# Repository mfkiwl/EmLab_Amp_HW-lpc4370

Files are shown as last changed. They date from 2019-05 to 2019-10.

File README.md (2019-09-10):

# EmLab Amp HW
Hardware for 80dB amp + digitizer

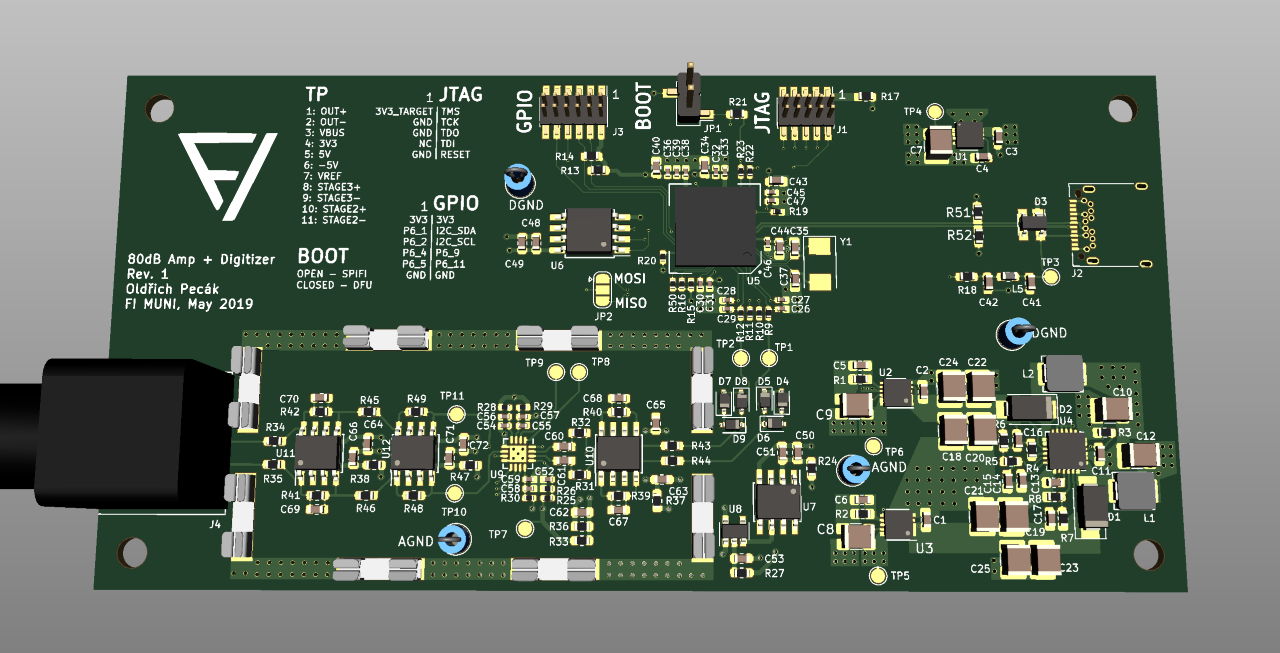
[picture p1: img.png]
Current Revision


## Notes
- the TPS65131 regulator does some weird stuff - maybe exchange for similar AD part?

## TODO
- debug prototype

### Schematic
- nothing

### PCB
- nothing

## Links
- [BOM](https://octopart.com/bom-tool/Xo4yGKYB)
- [LPC Link 2 Schematic](https://www.nxp.com/downloads/en/schematics/LPC-Link2-SCH.pdf)
- [BGA PCB Guidelines](https://www.nxp.com/docs/en/application-note/AN10778.pdf)
- [Proper grounding #1](https://www.analog.com/en/analog-dialogue/articles/staying-well-grounded.html)
- [Proper grounding #2](https://www.maximintegrated.com/en/app-notes/index.mvp/id/5450)
- [LPC4370 Datasheet](https://www.nxp.com/docs/en/data-sheet/LPC4370.pdf)
- [W25Q80BVSSIG Datasheet](https://openwrt.org/_media/media/datasheets/flash/w25q80bv.pdf)
- [IS25LP080D-JNLA3-TR](https://cz.mouser.com/ProductDetail/ISSI/IS25LP080D-JNLA3-TR?qs=sGAEpiMZZMuIiYGg9i1FDOSOPk6CUsSSrSt5PkokTOpe%2F19c4PAU8Q%3D%3D)
- [LT3094 Datasheet](https://www.analog.com/media/en/technical-documentation/data-sheets/LT3094.pdf)
- [LT3045 Datasheet] (https://www.analog.com/media/en/technical-documentation/data-sheets/3045fa.pdf)
- [TPS7A80 Datasheet](http://www.ti.com/lit/ds/symlink/tps7a80.pdf)
- [THS4131 Datasheet](http://www.ti.com/lit/ds/symlink/ths4131.pdf)
- [LMH6518 Datasheet](http://www.ti.com/lit/ds/symlink/lmh6518.pdf)

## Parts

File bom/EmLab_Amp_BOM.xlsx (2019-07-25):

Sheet: FARNELL
Počet desek: | 3 |  |  |  | Farnell
Manufacturer |  | Line Item | Počet(1 deska) | Celkem počet | URL
GCT |  | USB4085-GF-A | 1 | 3 | https://cz.farnell.com/gct-global-connector-technology/usb4085-gf-a/usb-connector-2-0-type-c-rcpt/dp/2924867
TE Connectivity |  | 1-1337543-0 | 1 | 3 | https://cz.farnell.com/greenpar-te-connectivity/1-1337543-0/rf-coaxial-bnc-right-angle-jack/dp/1020955
Vishay |  | CRCW04022K20FKED | 3 | 9 | https://cz.farnell.com/vishay/crcw04022k20fked/res-2k2-1-0-063w-0402-thick-film/dp/2140802
Vishay |  | CRCW04024K70FKEDHP | 3 | 9 | https://cz.farnell.com/vishay/crcw04024k70fkedhp/res-4k7-1-200mw-0402-thick-film/dp/1738858
Multicomp |  | MCWR04X1212FTL | 1 | 3 | https://cz.farnell.com/multicomp/mcwr04x1212ftl/res-12k1-1-0-0625w-thick-film/dp/2447105
Multicomp |  | MCWR06W1R00FTL | 2 | 6 | https://cz.farnell.com/multicomp/mcwr06w1r00ftl/res-1r-1-0-1w-0603-thick-film/dp/2447289
Vishay |  | CRCW060349R9FKEA | 2 | 6 | https://cz.farnell.com/vishay/crcw060349r9fkea/res-49r9-1-0-1w-0603-thick-film/dp/1469817
Multicomp |  | MCWR06X1000FTL | 2 | 6 | https://cz.farnell.com/multicomp/mcwr06x1000ftl/res-100r-1-0-1w-0603-thick-film/dp/2447227
Vishay |  | CRCW0603402RFKEA | 6 | 18 | https://cz.farnell.com/vishay/crcw0603402rfkea/res-402r-1-0-1w-0603-thick-film/dp/2141337
Vishay |  | CRCW06031K00FKEA | 1 | 3 | https://cz.farnell.com/vishay/crcw06031k00fkea/res-1k-1-0-1w-0603-thick-film/dp/1469740
Multicomp |  | MCWR06X2201FTL | 1 | 3 | https://cz.farnell.com/multicomp/mcwr06x2201ftl/res-2k2-1-0-1w-thick-film/dp/2447320
Vishay |  | CRCW06034K02FKEA | 7 | 21 | https://cz.farnell.com/vishay/crcw06034k02fkea/res-4k02-1-0-1w-0603-thick-film/dp/1469805
Multicomp |  | MCWR06X4701FTL | 2 | 6 | https://cz.farnell.com/multicomp/mcwr06x4701ftl/res-4k7-1-0-1w-0603-thick-film/dp/2447385
Vishay |  | CRCW060349K9FKEA | 2 | 6 | https://cz.farnell.com/vishay/crcw060349k9fkea/res-49k9-1-0-1w-0603-thick-film/dp/1652882
Multicomp |  | MCWR06X1003FTL | 1 | 3 | https://cz.farnell.com/multicomp/mcwr06x1003ftl/res-100k-1-0-1w-0603-thick-film/dp/2447226
Multicomp |  | MCWR06X1303FTL | 2 | 6 | https://cz.farnell.com/multicomp/mcwr06x1303ftl/res-130k-1-0-1w-thick-film/dp/2447247
Multicomp |  | MCWR06X5363FTL | 1 | 3 | https://cz.farnell.com/multicomp/mcwr06x5363ftl/res-536k-1-0-1w-0603-thick-film/dp/2694894
Panasonic |  | ERJ-3EKF6653V | 1 | 3 | https://cz.farnell.com/panasonic/erj3ekf6653v/res-665k-1-100mw-0603-thick-film/dp/2303304
Multicomp |  | MCWR06X1004FTL | 2 | 6 | https://cz.farnell.com/multicomp/mcwr06x1004ftl/res-1m-1-0-1w-0603-thick-film/dp/2447285
Multicomp |  | MC0402B104K250CT | 10 | 30 | https://cz.farnell.com/multicomp/mc0402b104k250ct/cap-0-1-f-25v-10-x7r-0402/dp/2320759
KEMET |  | C0402C470J5GACTU | 4 | 12 | https://cz.farnell.com/kemet/c0402c470j5gactu/cap-47pf-50v-5-c0g-np0-0402/dp/1414592
KEMET |  | C0402C103K3RACTU | 3 | 9 | https://cz.farnell.com/kemet/c0402c103k3ractu/cap-0-01-f-25v-10-x7r-0402/dp/1650806
Murata |  | GCM155R71E223KA55D | 2 | 6 | https://cz.farnell.com/murata/gcm155r71e223ka55d/cap-0-022-f-25v-10-x7r-0402/dp/2494188
KEMET |  | C0402C332K5RACTU | 1 | 3 | https://cz.farnell.com/kemet/c0402c332k5ractu/cap-3300pf-50v-10-x7r-0402/dp/1414590
KEMET |  | C0603C104M5RACTU | 12 | 36 | https://cz.farnell.com/kemet/c0603c104m5ractu/cap-0-1-f-50v-20-x7r-0603/dp/2581046
Murata |  | GRM188R61A106ME69D | 8 | 24 | https://cz.farnell.com/murata/grm188r61a106me69d/cap-10-f-10v-20-x5r-0603/dp/2456110
Yageo |  | CC0603KRX5R5BB475 | 3 | 9 | https://cz.farnell.com/yageo/cc0603krx5r5bb475/cap-4-7-f-6-3v-10-x5r-0603/dp/9402110
TDK |  | CGA3E3X7R1E474K080AB | 2 | 6 | https://cz.farnell.com/tdk/cga3e3x7r1e474k080ab/cap-0-47-f-25v-10-x7r-0603/dp/2210923
KEMET |  | C0603C103M5RACTU | 2 | 6 | https://cz.farnell.com/kemet/c0603c103m5ractu/cap-0-01-f-50v-20-x7r-0603/dp/2581043
KEMET |  | C0603C120J5GACTU | 2 | 6 | https://cz.farnell.com/kemet/c0603c120j5gactu/cap-12pf-50v-5-c0g-np0-0603/dp/1414612
KEMET |  | C0603C180J5GACAUTO | 2 | 6 | https://cz.farnell.com/kemet/c0603c180j5gacauto/cap-18pf-50v-5-c0g-np0-0603/dp/2821267
KEMET |  | C0603C680J5GACAUTO | 2 | 6 | https://cz.farnell.com/kemet/c0603c680j5gacauto/cap-68pf-50v-5-c0g-np0-0603/dp/2821269
Vishay |  | VJ0603A470KXAAC | 2 | 6 | https://cz.farnell.com/vishay/vj0603a470kxaac/cap-47pf-50v-10-c0g-np0-0603/dp/2896694
Murata |  | GCJ188R71E105KA01D | 1 | 3 | https://cz.farnell.com/murata/gcj188r71e105ka01d/cap-1-f-25v-10-x7r-0603/dp/2781410
KEMET |  | C0603C224K3RECAUTO | 1 | 3 | https://cz.farnell.com/kemet/c0603c224k3recauto/cap-0-22-f-25v-10-x7r-0603/dp/2708702

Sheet: MOUSER
Počet desek: | 3 |  |  |  | Mouser
Manufacturer |  | Line Item | Počet(1 deska) | Celkem počet | URL
NXP Semiconductors |  | LPC4370FET100E | 1 | 3 | https://cz.mouser.com/ProductDetail/NXP-Semiconductors/LPC4370FET100E
ISSI |  | IS25LP080D-JBLE | 1 | 3 | https://cz.mouser.com/ProductDetail/ISSI/IS25LP080D-JBLE
Texas Instruments |  | LMH6518SQE/NOPB | 1 | 3 | https://cz.mouser.com/ProductDetail/Texas-Instruments/LMH6518SQE-NOPB
Texas Instruments |  | THS4131ID | 3 | 9 | https://cz.mouser.com/ProductDetail/Texas-Instruments/THS4131ID?qs=sGAEpiMZZMsFOcXqMdeHCUfrMGQl6bAspOAcQWpNFhs%3D
Texas Instruments |  | TPS65131RGER | 1 | 3 | https://cz.mouser.com/ProductDetail/Texas-Instruments/TPS65131RGER
Analog Devices / Linear Technology |  | LT3094IDD#PBF | 1 | 3 | https://cz.mouser.com/ProductDetail/Analog-Devices-Linear-Technology/LT3094IDDPBF?qs=sGAEpiMZZMsGz1a6aV8DcJ5wwoift2gCGfC6lWVApcc%3D
Analog Devices |  | LT3045EDD#PBF | 1 | 3 | https://cz.mouser.com/ProductDetail/Analog-Devices-Linear-Technology/LT3045EDDPBF?qs=sGAEpiMZZMsGz1a6aV8DcG0CZsy7SJKshm5FSsNz7hU%3D
Texas Instruments |  | TPS7A8033DRBT | 1 | 3 | https://cz.mouser.com/ProductDetail/Texas-Instruments/TPS7A8033DRBT
Abracon |  | ABM3-12.000MHZ-D2Y-T | 1 | 3 | https://cz.mouser.com/ProductDetail/ABRACON/ABM3-12000MHZ-D2Y-T
Microchip |  | MCP601RT-I/OT | 1 | 3 | https://cz.mouser.com/ProductDetail/Microchip-Technology/MCP601RT-I-OT
Analog Devices |  | ADR421ARZ | 1 | 3 | https://cz.mouser.com/ProductDetail/Analog-Devices/ADR421ARZ
Nexperia |  | PRTR5V0U2X,215 | 1 | 3 | https://cz.mouser.com/ProductDetail/Nexperia/PRTR5V0U2X215
Bourns |  | SRP4012TA-5R6M | 1 | 3 | https://cz.mouser.com/ProductDetail/Bourns/SRP4012TA-5R6M
Bourns |  | SRP4012TA-4R7M | 1 | 3 | https://cz.mouser.com/ProductDetail/Bourns/SRP4012TA-4R7M
Harwin |  | S01-50250500 | 1 | 3 | https://cz.mouser.com/ProductDetail/Harwin/S01-50250500
Harwin |  | S2711-46R | 8 | 24 | https://cz.mouser.com/ProductDetail/Harwin/S2711-46R
MCC |  | SK34A-TP | 2 | 6 | https://cz.mouser.com/ProductDetail/Micro-Commercial-Components-MCC/SK34A-TP
Molex |  | 87898-0204 | 1 | 3 | https://cz.mouser.com/ProductDetail/Molex/87898-0204
FCI |  | 20021121-00010C4LF | 1 | 3 | https://cz.mouser.com/ProductDetail/Amphenol-FCI/20021121-00010C4LF
FCI |  | 20021121-00012C4LF | 1 | 3 | https://cz.mouser.com/ProductDetail/Amphenol-FCI/20021121-00012C4LF
Keystone |  | 5006 | 4 | 12 | https://cz.mouser.com/ProductDetail/Keystone-Electronics/5006
Diodes Inc. |  | 1N4148WS-7-F | 6 | 18 | https://cz.mouser.com/ProductDetail/Diodes-Incorporated/1N4148WSF-7
Yageo |  | RC0402FR-07100RL | 4 | 12 | https://cz.mouser.com/ProductDetail/Yageo/RC0402FR-07100RL
Yageo |  | RC0402FR-071RL | 3 | 9 | https://cz.mouser.com/ProductDetail/Yageo/RC0402FR-071RL
Yageo |  | RC0402FR-0710KL | 2 | 6 | https://cz.mouser.com/ProductDetail/Yageo/RC0402FR-0710KL
KEMET |  | C1210C475K3RACTU | 11 | 33 | https://cz.mouser.com/ProductDetail/KEMET/C1210C475K3RACTU?qs=sGAEpiMZZMs0AnBnWHyRQKLP9quIYhdR8bSQJSyuECw%3D
Murata |  | GCM32ER71E106KA57L | 2 | 6 | https://cz.mouser.com/ProductDetail/Murata-Electronics/GCM32ER71E106KA57K
Murata |  | GCM155R71E393JA55D | 1 | 3 | https://cz.mouser.com/ProductDetail/Murata-Electronics/GCM155R71E393JA55D
TDK |  | C1608X5R1E335K080AC | 1 | 3 | https://cz.mouser.com/ProductDetail/TDK/C1608X5R1E335K080AC

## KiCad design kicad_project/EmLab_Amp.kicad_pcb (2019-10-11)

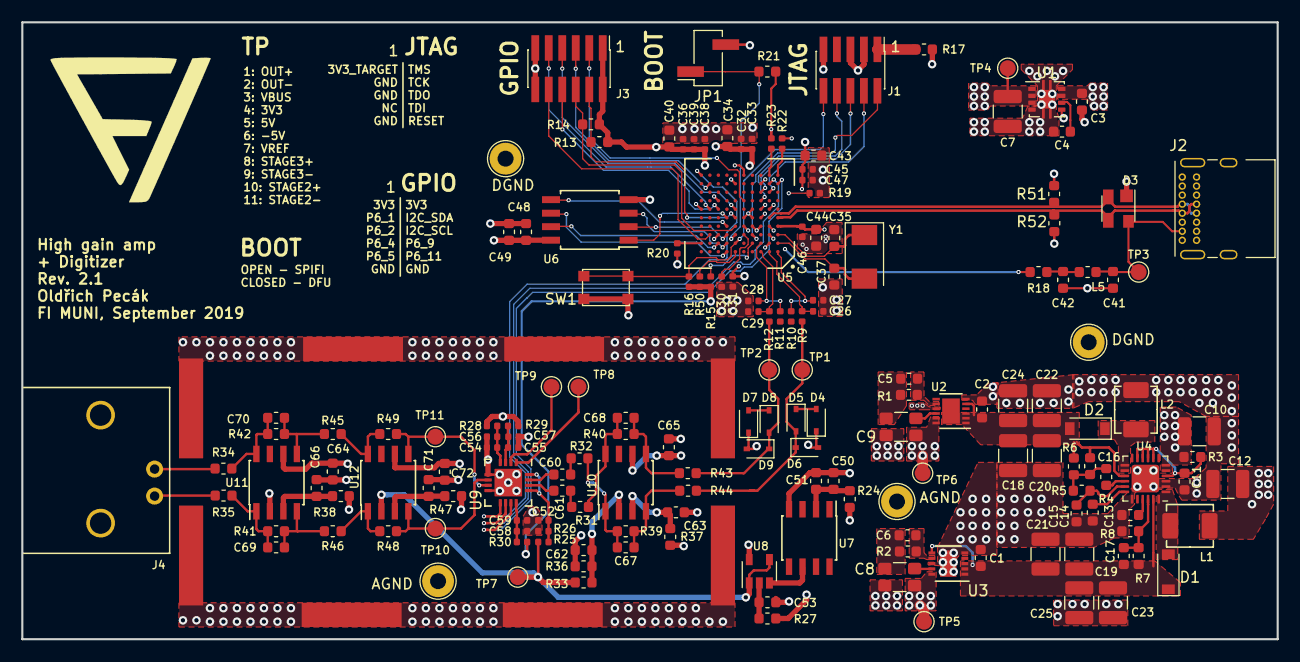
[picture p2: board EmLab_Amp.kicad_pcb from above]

Board: 4 copper layers, 118.1 x 58.0 mm, 170 parts (0 on the bottom side), 95 nets.

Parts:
AGND: TestPoint_Loop_D2.54mm_Drill1.5mm_Beaded
AGND#2: TestPoint_Loop_D2.54mm_Drill1.5mm_Beaded
C1, C2: 470n; C_0603_1608Metric
C3: 1u; C_0603_1608Metric
C4, C13: 10n; C_0603_1608Metric
C5, C6, C14: 4u7; C_0603_1608Metric
C7, C10, C12, C18, C19, C20, C21, C22, C23, C24, C25: 4u7; C_1210_3225Metric
C8, C9: 10u; C_1210_3225Metric_SPLIT
C11, C41, C48, C51, C53, C62, C63, C64, C65, C66, C71, C72: 100n; C_0603_1608Metric
C15: 220n; C_0603_1608Metric
C16, C17: 12p; C_0603_1608Metric
C26, C27, C28, C29: 47p; C_0402_1005Metric
C30, C31, C32, C36, C39, C45, C52, C56, C57, C58: 100n; C_0402_1005Metric
C33, C38: 22n; C_0402_1005Metric
C34, C40, C43, C44, C49, C50, C60, C61: 10u; C_0603_1608Metric
C35, C37: 18p; C_0603_1608Metric
C42: 3u3; C_0603_1608Metric
C46: 3n3; C_0402_1005Metric
C47: 39n; C_0402_1005Metric
C54, C55, C59: 10n; C_0402_1005Metric
C67, C68: 69p8; C_0603_1608Metric
C69, C70: 47p; C_0603_1608Metric
D1, D2: D_Schottky; D_SOD-123
D3: PRTR5V0U2X; SOT-143
D4, D5, D6, D7, D8, D9: 1N4148WS; D_SOD-323
DGND: TestPoint_Loop_D2.54mm_Drill1.5mm_Beaded
DGND#2: TestPoint_Loop_D2.54mm_Drill1.5mm_Beaded
J1: JTAG; PinHeader_2x05_P1.27mm_Vertical_SMD
J2: USB_C_Receptacle_USB2.0; USB_C_Receptacle_GCT_USB4085
J3: GPIO_EXP; PinHeader_2x06_P1.27mm_Vertical_SMD
J4: BNC; BNC_1337543
JP1: PinHeader_1x02_P2.54mm_Vertical_SMD_Pin1Right
L1: 4u7; BOURNS-SRP4012TA
L2: 5u6; BOURNS-SRP4012TA
L5: 1R resistor; L_0603_1608Metric
R1, R2: 49K9; R_0603_1608Metric
R3, R18: 100R; R_0603_1608Metric
R4: 100K; R_0603_1608Metric
R5, R8: 130K; R_0603_1608Metric
R6: 665K; R_0603_1608Metric
R7: 536K; R_0603_1608Metric
R9, R10, R11, R12: 100R; R_0402_1005Metric
R13, R14: 4K7; R_0603_1608Metric
R15, R16, R50: 4K7; R_0402_1005Metric
R17: 0R; R_0603_1608Metric
R19: 12K1; R_0402_1005Metric
R20, R22, R23: 2K2; R_0402_1005Metric
R21: 2K2; R_0603_1608Metric
R24, R27, R37, R38, R47: 1R; R_0603_1608Metric
R25, R26: 10K; R_0402_1005Metric
R28, R29, R30: 1R; R_0402_1005Metric
R31, R32, R34, R35, R45, R46: 400R; R_0603_1608Metric
R33, R39, R40, R48, R49: 4K; R_0603_1608Metric
R36: 1K; R_0603_1608Metric
R41, R42: 40K; R_0603_1608Metric
R43, R44: 50R; R_0603_1608Metric
R51, R52: 1M; R_0603_1608Metric
SW1: RST BTN; SW_SPST_PTS810
TP1: OUT+; TestPoint_Pad_D1.5mm
TP2: OUT-; TestPoint_Pad_D1.5mm
TP3: VBUS; TestPoint_Pad_D1.5mm
TP4: 3V3; TestPoint_Pad_D1.5mm
TP5: 5V; TestPoint_Pad_D1.5mm
TP6: -5V; TestPoint_Pad_D1.5mm
TP7: V_REF; TestPoint_Pad_D1.5mm
TP8: Stage3+; TestPoint_Pad_D1.5mm
TP9: Stage3-; TestPoint_Pad_D1.5mm
TP10: Stage2+; TestPoint_Pad_D1.5mm
TP11: Stage2-; TestPoint_Pad_D1.5mm
U1: TPS7A80; TI-VSON-8
U2: LT3094xDD; DFN-12-1EP_3x3mm_P0.45mm_EP1.66x2.38mm
U3: LT3045xDD; DFN-10-1EP_3x3mm_P0.5mm_EP1.55x2.48mm
U4: TPS6513x; QFN-24-1EP_4x4mm_P0.5mm_EP2.6x2.6mm
U5: LPC4370-TFBGA100; BGA-100_10x10_10.0x10.0mm
U6: IS25LP080D; SOIJ-8_5.3x5.3mm_P1.27mm
U7: ADR421; SOIC-8_3.9x4.9mm_P1.27mm
U8: MCP601R; SOT-23-5
U9: LMH6518; QFN-16-1EP_4x4mm_P0.5mm_EP2.6x2.6mm
U10, U11, U12: THS4131ID; SOIC-8_3.9x4.9mm_P1.27mm
Y1: 12MHz Crystal; Crystal_SMD_Abracon_ABM3-2Pin_5.0x3.2mm

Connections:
+3V3: C7.1, C31.1, C32.1, C33.1, C34.1, C36.1, C38.1, C39.1, C40.1, C43.1, C44.1, C45.1, C46.1, C47.1, C48.1, C49.1, J3.1, J3.2, R13.1, R14.1, R15.1, R16.1, R17.2, R21.1, R23.1, R30.1, R50.1, TP4.1, U1.1, U1.2, U1.3, U5.B2, U5.D1, U5.D2, U5.E4, U5.E5, U5.F4, U5.F10, U5.K5, U6.8
+5V: C8.2, R24.1, R27.1, R28.1, R29.1, R37.1, R38.1, R47.1, TP5.1, U3.9, U3.10
-5V: C9.2, C65.2, C66.2, C72.2, TP6.1, U2.10, U2.11, U2.12, U10.6, U11.6, U12.6
/Amplifier/S3_CS: U5.K10, U9.9
/Amplifier/S3_DIO: U5.J2, U9.10
/Amplifier/S3_SCLK: U5.J1, U9.11
/Amplifier/STAGE2_NEG: R49.2, TP11.1, U9.7, U12.5
/Amplifier/STAGE2_POS: R48.1, TP10.1, U9.6, U12.4
/Amplifier/V_REF: R25.1, R33.1, TP7.1, U8.1, U8.4, U12.2
/LPC4370-GPIO/BOOT_0: R23.2, U5.K2
/LPC4370-GPIO/BOOT_1: R22.1, U5.K1
/LPC4370-GPIO/BOOT_2: JP1.1, R21.2, U5.C6
/LPC4370-GPIO/BOOT_3: R20.1, U5.B10
/LPC4370-GPIO/GPIO_0: J3.3, U5.G5
/LPC4370-GPIO/GPIO_1: J3.5, U5.J9
/LPC4370-GPIO/GPIO_2: J3.7, U5.F6
/LPC4370-GPIO/GPIO_3: J3.9, U5.F9
/LPC4370-GPIO/GPIO_4: J3.8, U5.F8
/LPC4370-GPIO/GPIO_5: J3.10, U5.C9
/LPC4370-GPIO/I2C_SCL: J3.6, R14.2, U5.D6
/LPC4370-GPIO/I2C_SDA: J3.4, R13.2, U5.E6
/LPC4370-GPIO/SPIFI_CS: U5.E7, U6.1
/LPC4370-GPIO/SPIFI_MISO: U5.C7, U6.2
/LPC4370-GPIO/SPIFI_MOSI: U5.D7, U6.5
/LPC4370-GPIO/SPIFI_SCK: U5.A7, U6.6
/LPC4370-GPIO/SPIFI_SIO2: U5.B7, U6.3
/LPC4370-GPIO/SPIFI_SIO3: U5.B8, U6.7
/LPC4370-JTAG-PWR-MISC/ADC0: D5.2, D6.1, R9.2, R44.2, TP1.1
/LPC4370-JTAG-PWR-MISC/ADC3: D8.2, D9.1, R12.2, R43.1, TP2.1
/LPC4370-JTAG-PWR-MISC/DBGEN: R50.2, U5.A6
/LPC4370-JTAG-PWR-MISC/RESET: J1.10, R16.2, SW1.1, U5.B6
/LPC4370-JTAG-PWR-MISC/TCK: J1.4, U5.H2
/LPC4370-JTAG-PWR-MISC/TDI: J1.8, U5.G3
/LPC4370-JTAG-PWR-MISC/TDO: J1.6, U5.H3
/LPC4370-JTAG-PWR-MISC/TMS: J1.2, U5.C4
/LPC4370-JTAG-PWR-MISC/TRST: R15.2, U5.B4
/LPC4370-USB/USB_VBUS: C3.1, C10.1, C12.1, C41.1, D3.4, J2.A4, J2.A9, J2.B4, J2.B9, L1.1, L5.2, R3.2, TP3.1, U1.5, U1.7, U1.8, U4.5, U4.6
/Power/VNEG: C2.2, C16.2, C18.1, C20.1, C22.1, C24.1, D2.2, R6.2, U2.1, U2.2, U2.3, U2.5, U2.13, U4.15
/Power/VPOS: C1.2, C17.1, C19.1, C21.1, C23.1, C25.1, D1.1, R7.1, U3.1, U3.2, U3.3, U3.6, U4.23
GND: AGND.1, AGND#2.1, C1.1, C2.1, C3.2, C4.2, C5.1, C6.1, C7.2, C8.1, C9.1, C10.2, C11.2, C12.2, C13.2, C14.2, C15.2, C18.2, C19.2, C20.2, C21.2, C22.2, C23.2, C24.2, C25.2, C26.2, C27.2, C28.2, C29.2, C30.2, C31.2, C32.2, C33.2, C34.2, C35.2, C36.2, C37.2, C38.2, C39.2, C40.2, C41.2, C42.2, C43.2, C44.2, C45.2, C46.2, C47.2, C48.2, C49.2, C50.1, C51.1, C52.1, C53.1, C54.1, C55.1, C56.1, C57.1, C58.1, C59.1, C62.1, C63.1, C64.1, C65.1, C66.1, C71.1, C72.1, D3.1, D4.1, D6.2, D7.1, D9.2, DGND.1, DGND#2.1, J1.3, J1.5, J1.9, J2.A1, J2.A12, J2.B1, J2.B12, J2.S1, J3.11, J3.12, J4.2, JP1.2, L2.2, R1.1, R2.1, R8.2, R19.2, R20.2, R22.2, R26.1, R35.1, R36.1, R51.2, R52.2, SW1.2, U1.4, U1.9, U2.6, U2.9, U3.5, U3.8, U3.11, U4.2, U4.3, U4.19, U4.25, U5.C2, U5.C8, U5.D3, U5.D4, U5.D5, U5.F2, U5.G8, U5.J3, U5.J6, U6.4, U7.4, U8.5, U9.5, U9.8, U9.17, U11.2
unnamed: C4.1, U1.6
unnamed: C5.2, R1.2, U2.8
unnamed: C6.2, R2.2, U3.7
unnamed: C11.1, R3.1, U4.4, U4.8, U4.9, U4.10, U4.11
unnamed: C13.1, U4.21
unnamed: C14.1, U4.18
unnamed: C15.1, R5.1, U4.17
unnamed: C16.1, R4.1, R5.2, R6.1
unnamed: C17.2, R7.2, R8.1, U4.22
unnamed: C26.1, R9.1, U5.A2
unnamed: C27.1, R10.1, U5.A1
unnamed: C28.1, R11.1, U5.B3
unnamed: C29.1, R12.1, U5.A3
unnamed: C30.1, U5.C5
unnamed: C35.1, U5.C1, Y1.1
unnamed: C37.1, U5.B1, Y1.2
unnamed: C42.1, L5.1, R18.2
unnamed: C50.2, C51.2, R24.2, U7.2
unnamed: C52.2, R25.2, R26.2, U9.13, U9.16
unnamed: C53.2, R27.2, U8.2
unnamed: C54.2, C56.2, R28.2, U9.4
unnamed: C55.2, C57.2, R29.2, U9.3
unnamed: C58.2, C59.2, R30.2, U9.12
unnamed: C60.1, U9.15
unnamed: C60.2, R32.1
unnamed: C61.1, U9.14
unnamed: C61.2, R31.2
unnamed: C62.2, R33.2, R36.2, U10.2
unnamed: C63.2, R37.2, U10.3
unnamed: C64.2, R38.2, U11.3
unnamed: C67.1, R39.2, R44.1, U10.4
unnamed: C67.2, R32.2, R39.1, U10.1
unnamed: C68.1, R40.2, R43.2, U10.5
unnamed: C68.2, R31.1, R40.1, U10.8
unnamed: C69.1, R41.2, R46.1, U11.4
unnamed: C69.2, R35.2, R41.1, U11.1
unnamed: C70.1, R42.2, R45.2, U11.5
unnamed: C70.2, R34.1, R42.1, U11.8
unnamed: C71.2, R47.2, U12.3
unnamed: D1.2, L1.2, U4.1, U4.24
unnamed: D2.1, L2.1, U4.13, U4.14
unnamed: D3.2, J2.A7, J2.B7, R51.1, U5.E2
unnamed: D3.3, J2.A6, J2.B6, R52.1, U5.E1
unnamed: D4.2, D5.1
unnamed: D7.2, D8.1
unnamed: J1.1, R17.1
unnamed: J4.1, R34.2
unnamed: R4.2, U4.16
unnamed: R18.1, U5.E3
unnamed: R19.1, U5.F3
unnamed: R45.1, R49.1, U12.8
unnamed: R46.2, R48.2, U12.1
unnamed: TP8.1, U9.1
unnamed: TP9.1, U9.2
unnamed: U7.6, U8.3

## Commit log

2019-03-12 add gerber and drill files to .gitignore
2019-03-13 Add kicad project
    [EmLab_Amp.kicad_pcb, EmLab_Amp.sch]
2019-03-27 LPC4370 misc, jtag, power
    [EmLab_Amp.sch, LPC4370-JTAG-PWR-MISC.sch, Power.sch]
2019-03-27 add USB interface
    [EmLab_Amp.sch, LPC4370-JTAG-PWR-MISC.sch, LPC4370-USB.sch, Power.sch]
2019-04-01 add LPC4370 gpio
    [EmLab_Amp.sch, LPC4370-GPIO.sch, LPC4370-JTAG-PWR-MISC.sch, LPC4370-USB.sch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]
2019-04-03 Add power supplies
    [EmLab_Amp.sch, LPC4370-GPIO.sch, LPC4370-JTAG-PWR-MISC.sch, LPC4370-USB.sch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]
2019-04-15 Amplifier stage 1 and 2
    [Amplifier.sch, EmLab_Amp.sch, LPC4370-GPIO.sch, LPC4370-JTAG-PWR-MISC.sch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]
2019-04-17 Amplifier stage 3&4, v_ref
    [Amplifier.sch, EmLab_Amp.sch, LPC4370-GPIO.sch, LPC4370-JTAG-PWR-MISC.sch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]
2019-04-17 Schematic done, Rev1
    [Amplifier.sch, EmLab_Amp.sch, LPC4370-GPIO.sch, LPC4370-JTAG-PWR-MISC.sch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]
2019-05-08 Start on PCB
    [Amplifier.sch, EmLab_Amp.kicad_pcb, EmLab_Amp.sch, LPC4370-GPIO.sch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]
2019-05-08 PCB: Amplifier done, digital done
    [Amplifier.sch, EmLab_Amp.kicad_pcb, EmLab_Amp.sch, LPC4370-GPIO.sch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]
2019-05-09 PCB: finished analog and digital
    [Amplifier.sch, EmLab_Amp.kicad_pcb, EmLab_Amp.sch, LPC4370-GPIO.sch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]
2019-05-10 PCB layout done
    [EmLab_Amp.kicad_pcb, LPC4370-USB.sch, Power.sch]
2019-05-13 PCB rev. 1 done
    [EmLab_Amp.kicad_pcb]
2019-05-20 PCB - add GND test points
    [EmLab_Amp.kicad_pcb]
2019-05-24 manufacturing files
    [EmLab_Amp.kicad_pcb]
2019-07-12 Change USB connector
    [EmLab_Amp.kicad_pcb, LPC4370-USB.sch]
2019-07-25 add BOM
    [EmLab_Amp.kicad_pcb, EmLab_Amp_BOM.xlsx]
2019-09-23 Rev 2
    [Amplifier.sch, EmLab_Amp.kicad_pcb, EmLab_Amp.sch, LPC4370-GPIO.sch]
2019-09-23 iBom + formatting PCB
    [EmLab_Amp.kicad_pcb]
2019-10-11 rev 2.1
    [Amplifier.sch, EmLab_Amp.kicad_pcb, EmLab_Amp.sch, LPC4370-GPIO.sch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]
